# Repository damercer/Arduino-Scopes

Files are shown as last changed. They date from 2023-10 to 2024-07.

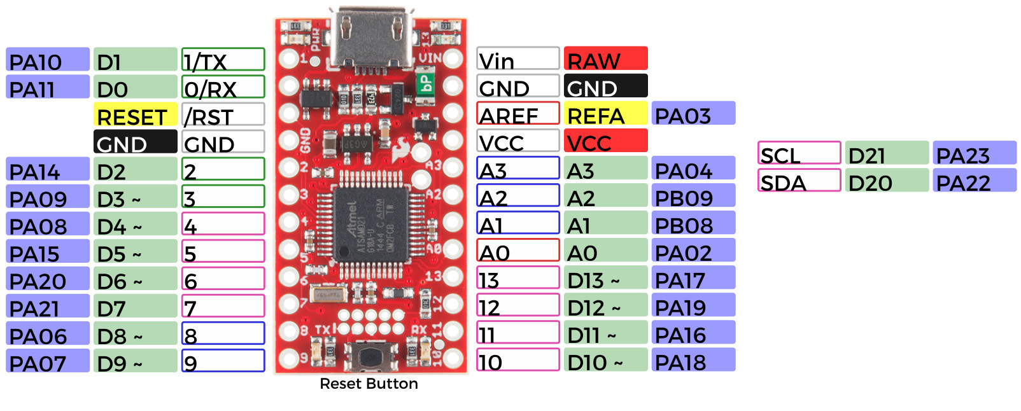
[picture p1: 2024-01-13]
SparkFun-SAMD21_pwm_awg/board-mini-overview-2.jpg

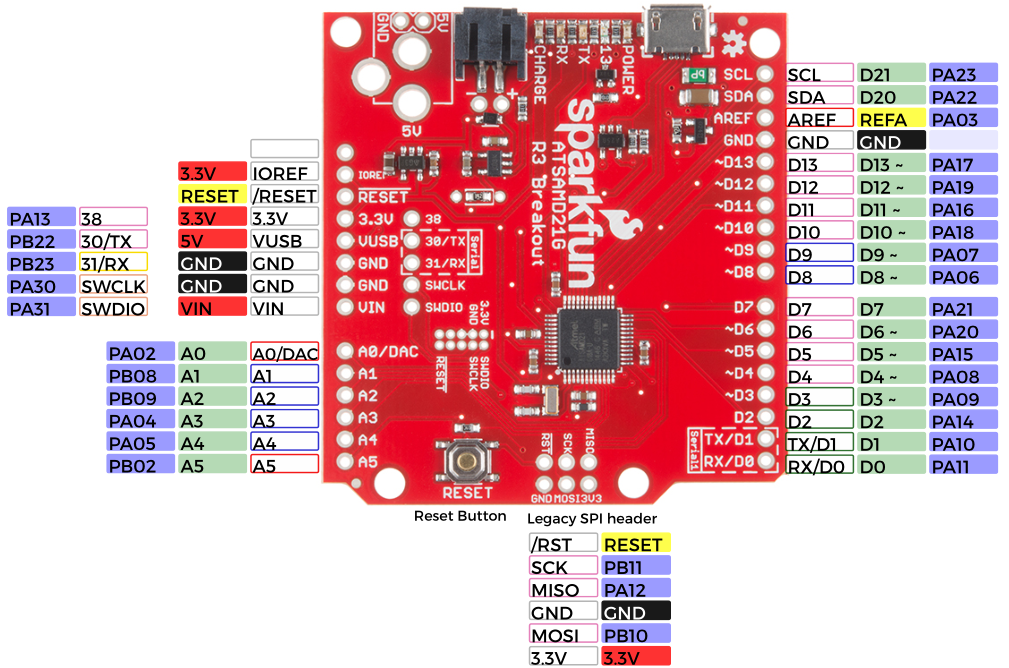
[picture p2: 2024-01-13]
SparkFun-SAMD21_pwm_awg/board-dev-overview.png

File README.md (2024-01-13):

# Arduino firmware for Universal-ALICE
With the goal of "Instrumentation for Every Student" in mind this project is intended to lower all barriers to providing a hardware and software platform for teaching electronic circuits to engineering students. Every student should have access to affordable hardware and software to measure their experiments.
This project offers a free open source software user interface that is compatible with hardware produced in large quantities at low cost (ranging from $5 to $20) from multiple suppliers.
#
Currently available hardware interfaces (some are works in progress):

* Arduino compatible microcontroler boards:
  + Adafruit QT Pi - SAMD21
  + Adafruit Trinket M0 (ATSAMD21)
  + Adafruit ItsyBitsy M0 Express (ATSAMD21)
  + Adafruit ItsyBitsy M4 Express (ATSAMD51)
  + Raspberry Pi Pico RP-2040
    - With external R/2R DAC or SPI DAC or PWM analog AWG output
  + SparkFun SAMD21 Mini Breakout (DEV-13664)
  + SparkFun Thing Plus - SAMD51 (DEV-14713)
  + Seeed Studio XIAO SAMD21
  + Seeed Studio XIAO RP-2040
    - With external SPI DAC or PWM analog AWG output

If you are not a technical individual or highly familiar with computer operating systems and you have your choice of computers, a Windows computer is highly recommended. You will usually run into fewer issues, if any, with that operating system.

Known Issues: If your computer encrypts files saved on external storge devices (USB disk drives) then the UF2 Bootloader method of flashing firmware to micro-controller boards will not work. You would need to use a different computer that does not encrypt files or consult your local system administrator.

Linux Operating system: On Linux computers access to USB based serial comms devices is not allowed for non root users by default. A udev rules file needs to be added. Place the 99-arduino.rules from this repository in etc/udev/rules.d

It contains one line per board / vendor:

SUBSYSTEMS=="usb", ATTRS{idVendor}=="802F", ATTRS{idProduct}=="2886", GROUP="dialout", MODE="0666"

The above idVendor value is board / vendor specific and may need to be adjusted to match your specific board(s). The one above is specifically for the XIAO SAMD21 board.

If this rules file does not work on your version of Linux there may be other things like this that work. Searching the web on how to make serial USB devices work may provide an alternate solution or consult with your local Linux expert.

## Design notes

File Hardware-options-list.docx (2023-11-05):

This Document.

This document lists various hardware options for very low cost personal instrumentation. These are listed in order by cost / ease of implementation / solderless breadboard friendliness.

Summary:

There are some basic assumptions.

First is that the hardware is part of the Arduino ecosystem and the embedded firmware is developed using the Arduino IDE.

Most all hardware platforms in the Arduino world have built in ADCs of some speed / resolution so any / all can provide a basic analog input / “oscilloscope” type instrument. They also generally provide at least one fixed DC power supply voltage available for the user. Digital inputs and outputs are available with one or more that can be programed as square wave PWM outputs.

Very few if any have internal DAC analog output(s) that could provide an analog waveform generator output (AWG) function. External components, such as serial (SPI) DAC integrated circuits, generally need to be added to generate analog waveforms. These add-on external circuits (modules) add cost and wiring complexity up to and including mounting everything on a carrier PCB which adds labor and cost.

As an alternate, but less desire able solution, analog outputs can be generated by modulating and low pass filtering one or more digital PWM outputs. The added cost could be as little as a passive resistor and capacitor but the output will not be buffered. A buffer op-amp or active filter circuit could be added.

The options presented here provide some solutions that provide various levels of cost, performance and complexity.

Version based on XIAO SAMD21

Performance Specs:

- Up to 3 12 bit Scope channels, 50 KSPS for one channel, 25 KSPS per channel for two channels or 16.667 KSPS for all three channels.
- One 8 bit AWG channel at 50 KSPS
- Up to 6 digital input channels at same sample rate as analog scope
- 1 PWM digital output or 1 PWM “analog” AWG output

Parts List: Total, $ 5.40 (plus import Tariff)

Seeed Studio XIAO SAMD21:

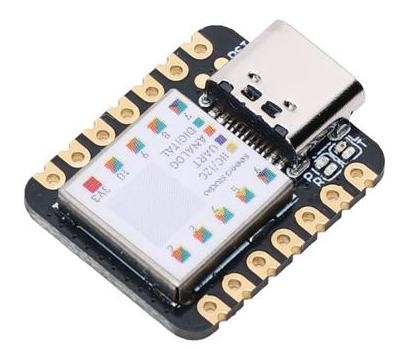
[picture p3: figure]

Many experiment setups can be done with just the one 14 pin module, so with installed male pin headers it can be easily inserted into a solderless breadboard and effectively becomes just another “part” in the experimental setup.

Solderless Breadboard Layout:

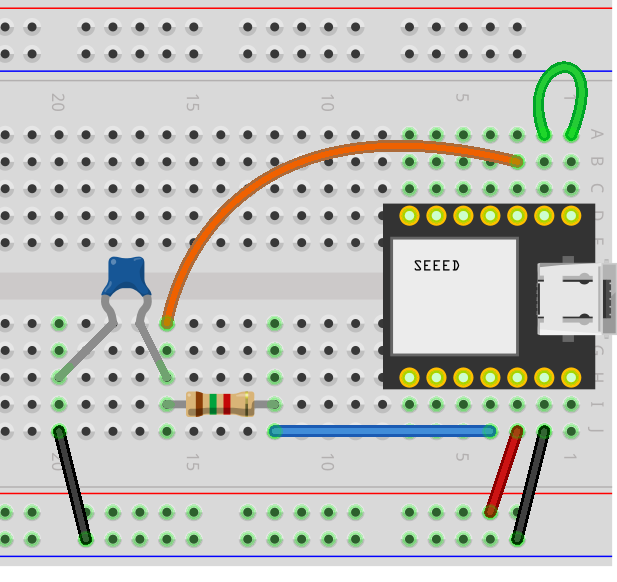
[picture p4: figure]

Includes RC low pass filter on PWM AWG output.

Version based on XIAO RP2040 + SPI DAC

Performance Specs:

- Up to 3 12 bit Scope channels at up to 200 KSPS for one channel, 125 KSPS for 2 channels, 83.333 KSPS for three channels.
- Up to two 8/10/12 bit AWG channels at 50 KSPS.
- Up to 4 digital input channels at same sample rate as analog scope.

Parts List: Total, $ 9.13 (plus import Tariff)

Seeed Studio XIAO RP2040:

- Price: Unit Price: $5.40 (plus import Tariff)
- Digi-Key Part Number: 1597-102010428-ND
- Manufacturer: Seeed Technology Co., Ltd
- Manufacturer Product Number: 102010428
- Description: SEEED STUDIO XIAO RP2040 ARDUINO

Dual DAC for AWG outputs: MCP4922-E/P

- Unit Price: $3.73
- Digi-Key Part Number, MCP4922-E/P-ND
- Manufacturer :Microchip Technology
- Manufacturer Product Number: MCP4922-E/P
- Description: IC DAC 12BIT V-OUT 14DIP

Alternate Dual DAC for AWG outputs: MCP4822-E/P

- Unit Price: $4.28
- Digi-Key Part Number, MCP4822-E/P-ND
- Manufacturer :Microchip Technology
- Manufacturer Product Number: MCP4822-E/P
- Description: IC DAC 12BIT V-OUT 8DIP

Alternate 10 and 8 bit dual DACs:

- MCP4812-E/P, $3.01
- MCP4802-E/P, $2.11
- LTC1661CN8, $5.43, 10BIT V-OUT 8DIP
- AD7303BNZ, $11.24, 8BIT V-OUT 8DIP

Again only the two components and some wires are used in this scheme so even more solderless breadboard friendly with the 14 pin XIAO module vs the 40 pin Pi Pico Module.

Solderless Breadboard Layout including two DAC reconstruction low pass filters.

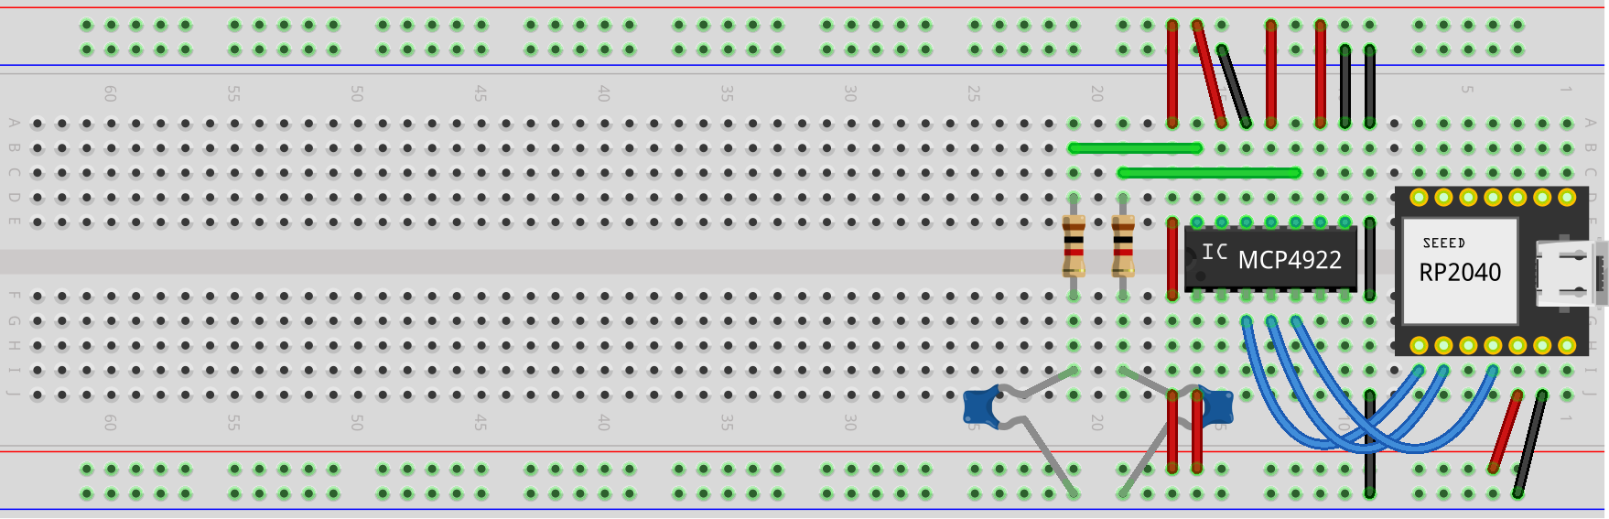
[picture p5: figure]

For relative size comparison.

The XIAO module along with SPI DAC could additionally be permanently mounted on a solder breadboard such as this one from Digi-Key: Cost $1.48.

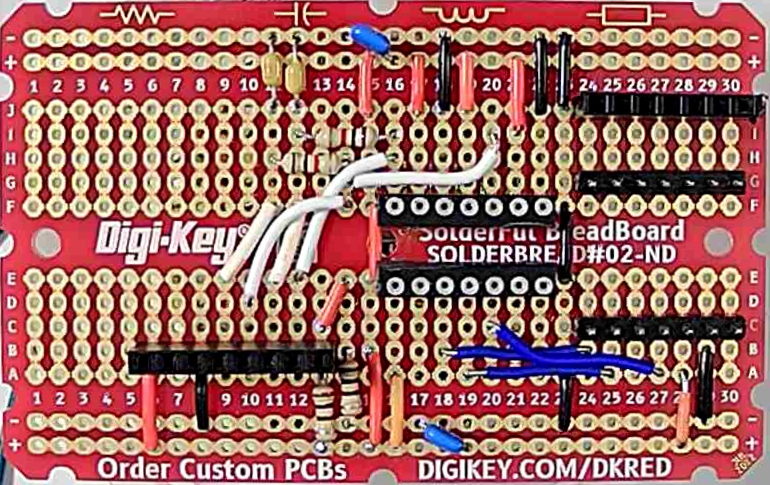
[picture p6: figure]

Solder breadboard wiring without active components installed

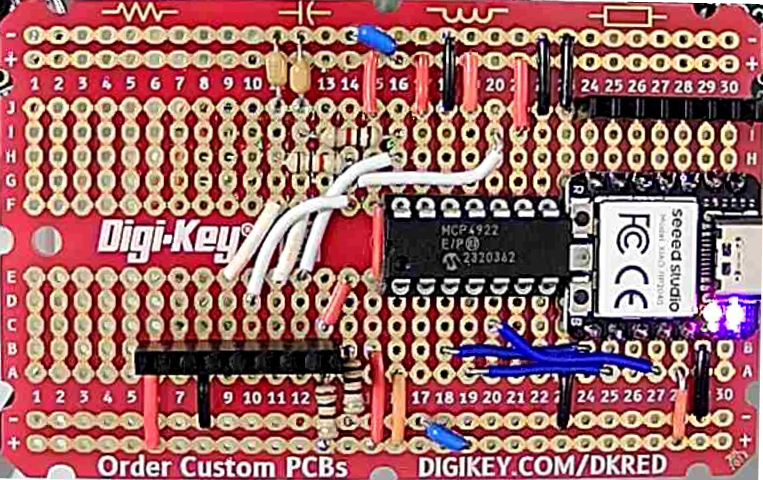
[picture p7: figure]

Solder breadboard wiring with active components installed

Digi-Key part number: DKS-SOLDERBREAD-02, 30 ROW SOLDERFUL BREADBOARD

Breadboard, General Purpose Plated Through Hole (PTH) 5 Hole Pad (Both Sides) 0.100" (2.54mm)

Version based on Raspberry Pi Pico + SPI DAC

Performance Specs:

- Up to 3 12 bit Scope channels at up to 200 KSPS for one channel, 125 KSPS for 2 channels, 83.333 KSPS for three channels.
- Up to two 8/10/12 bit AWG channels at 50 KSPS.
- Up to 8 digital input channels at same sample rate as analog scope.
- 1 PWM digital output.

Parts List: Total, $ 8.73 (plus import Tariff)

Raspberry Pi Pico RP2040 with headers:

- Unit price: $5.00 ($4.00 w/o headers)
- Digi-Key Part Number: 2648-SC0917-ND
- Manufacturer: Raspberry Pi, Manufacturer Product Number SC0917
- Description :RASPBERRY PI PICO H RP2040 Detailed Description :RP2040 Raspberry Pi Pico - ARM® Cortex®-M0+ MCU 32-Bit Embedded Evaluation Board

Dual DAC for AWG outputs: MCP4922-E/P

- Unit Price: $3.73
- Digi-Key Part Number, MCP4922-E/P-ND
- Manufacturer :Microchip Technology
- Manufacturer Product Number: MCP4922-E/P
- Description: IC DAC 12BIT V-OUT 14DIP

Alternate Dual DAC for AWG outputs: MCP4822-E/P

- Unit Price: $4.28
- Digi-Key Part Number, MCP4822-E/P-ND
- Manufacturer :Microchip Technology
- Manufacturer Product Number: MCP4822-E/P
- Description: IC DAC 12BIT V-OUT 8DIP

Alternate 10 and 8 bit dual DACs:

- MCP4912, MCP4812-E/P, $3.01
- MCP4902, MCP4802-E/P, $2.11
- LTC1661CN8, $5.43, 10BIT V-OUT 8DIP
- AD7303BNZ, $11.24, 8BIT V-OUT 8DIP

Only the two components and some wires are used in this scheme so somewhat solderless breadboard friendly.

Solderless breadboard layout (minus DAC reconstruction filter):

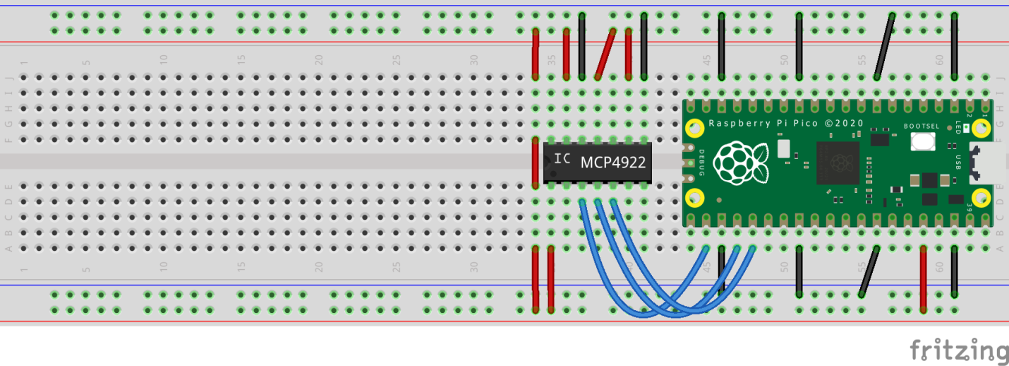
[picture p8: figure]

For relative size comparison. About ½ of a full length breadboard is needed.

Version based on Raspberry Pi Pico + Resistor Networks

Performance Specs:

- Up to 3 12 bit Scope channels at up to 200 KSPS for one channel, 125 KSPS for 2 channels, 83.333 KSPS for three channels.
- Up to two 8 bit AWG channels at 100 KSPS
- Up 6 digital input channels at same sample rate as analog scope
- 1 PWM digital output

List of Hardware:

Total parts cost less than $10 not including any PCB to mount parts on or a full length solderless breadboard.

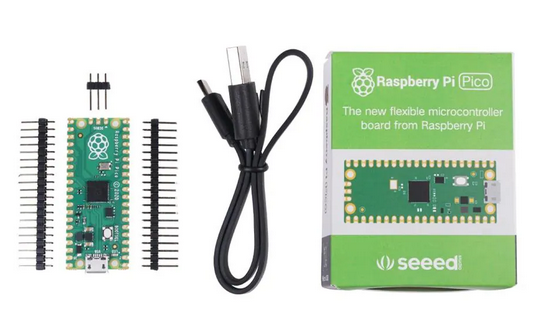
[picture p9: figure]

Pi Pico Board Basic Kit $6.38 each or $4.00 for just board no headers or $5.00 with installed headers: (SC0915 Description RASPBERRY PI PICO RP2040)

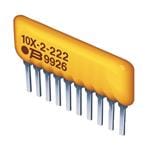
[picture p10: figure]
Bourns 4606X-R2R-103LF Enlarged Image

2X - 10 K R/2R ladder network for AWG DACs $ 0.51 each (4606X-R2R-103LF) at Mouser $0.71 at Digi-Key

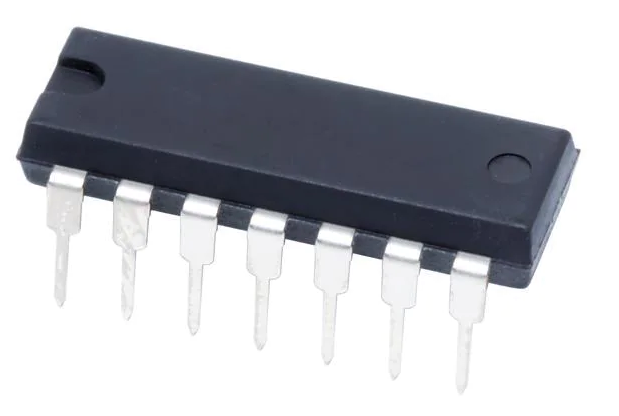
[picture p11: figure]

2X - LM324 Quad Op-amp for AWG DAC buffers / Scope Input buffers $0.59 each at Mouser $0.11 at Digi-Key

Up to 16 – 20 1/8 watt resistors various values.

Not particularly solderless breadboard friendly so a PCB to mount everything will be a useful approach.

PC Board Layout:

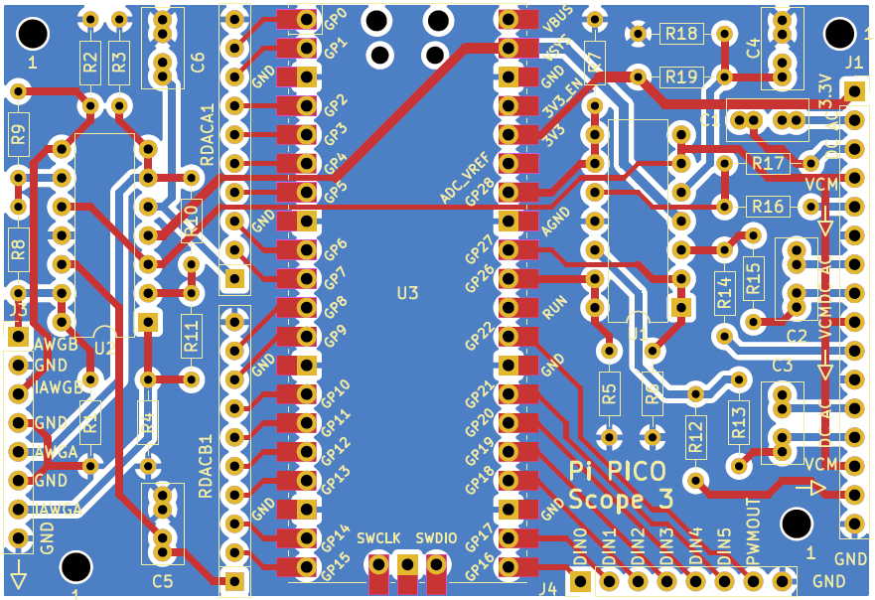
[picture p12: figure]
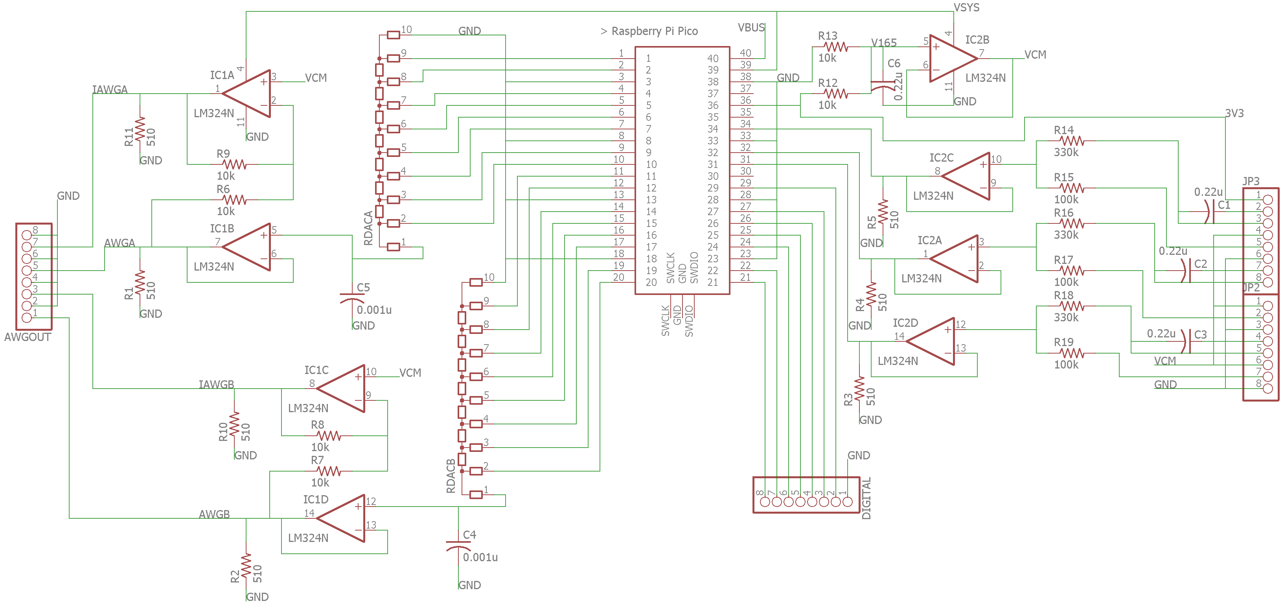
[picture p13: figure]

PCB Schematic

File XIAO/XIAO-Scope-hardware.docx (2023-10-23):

Seeed Studio XIAO SAMD21 as an introductory personal instrument.

Objective:

To demonstrate the use of the Seeed Studio XIAO SAMD21 micro-controller board as a personal lab data measurement system in introductory level circuits (and electronics) courses.

Hardware:

Seeed Studio XIAO SAMD21 micro-controller board. Cost $5.40 (Digi-Key Part Number 1597-102010328-ND)

The XIAO board is a small 14 pin DIP like module. By installing male pin headers it can be easily inserted into a solderless breadboard and effectively becomes just another “part” in the experimental setup.

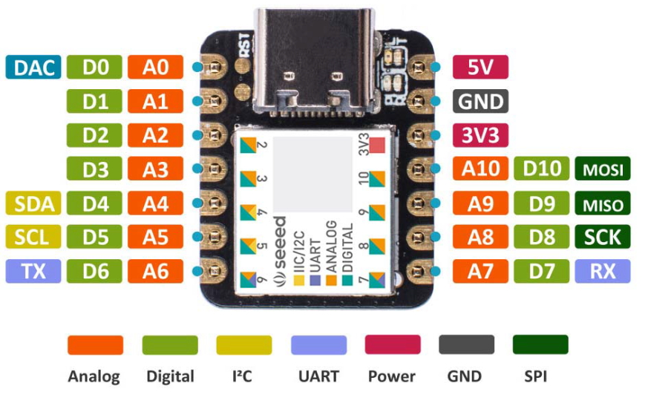
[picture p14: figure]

XIAO pinout

The XIAO contains one 12 bit ADC which can be multiplexed to multiple pins. It also contains one 10 bit DAC available on pin A0. The overall maximum ADC sample rate (50 KSPS) will be shared by the scope input channels and the per channel sample rate will depend on the number of analog input pins being measured. The XIAO can also generate a PWM digital output on pin D10. This PWM output can also be modulated and low pass filtered to provide a pseudo second AWG output channel (B). Using the PWM output as a second AWG output will cut the analog DAC sample rate essentially in half.

The remaining 6 digital input pins (D4 – D9) can optionally be sampled along with the analog inputs to provide a kind of “mixed signal” scope display.

None of the XIAO pins are 5 V tolerant and will likely be damaged if voltages beyond 0 and 3.3V are applied. The XIAO SAMD21 is a 3.3 volts device and applying 5 volts to an input will overload and damage the XIAO. There may be a 5-volt power connection on the board, but DO NOT use it to power experiments unless you are certain of the voltages of any nodes you might be measuring with one of the input pins. Absolute Maximum Pin voltage with respect to GND - GND-0.6V and VDD - VDD+0.6V.

USB C to USB A cable.

Solderless breadboard.

Various components, resistors, capacitors, diodes …

Board Firmware:

Developed using the Arduino IDE.

Download the Arduino IDE from here: https://www.arduino.cc/en/software

Seeed Studio Getting Started web page (contains info on configuring Arduino IDE for XIAO): https://wiki.seeedstudio.com/Seeeduino-XIAO/

How to Add Seeed boards to Arduino IDE: (from https://wiki.seeedstudio.com/Seeed_Arduino_Boards/)

Open the Arduino IDE, click on File > Preferences, and copy the below url to the Additional Boards Manager URLs list:

https://files.seeedstudio.com/arduino/package_seeeduino_boards_index.json

Click on Tools > Board > Board Manager. Now search the board by name, “Seeeduino XIAO”

Click on Tools > Ports and select the correct COM port for the board.

Open the Source file: XIAO_Scope_pwm_awg.ino

Click on the Upload arrow button.

PC Host Software:

ALICE Universal, PC Host User Interface developed using Python 3.10 and XIAO hardware specific interface code also developed using Python 3.10 (PySerial library required). Source code and configuration files:

Alice-universal-alpha.pyw

alice_init.ini

XIAO_3a_1w_6d_Interface_Level.py

Demonstration Lab Examples:

The test circuit schematic shown in figure 1 and breadboard layout shown in figure 2 is used to illustrate how the micro-controller hardware is connected to a simple R-C low pass circuit. The R-C test circuit consists of R1 and C1. The “grounded” end of C1 is connected to a resistor divider (R2 and R3) between GND (black wire) and the 3.3V power supply (red wire).

The voltage at the divider will be 3.3V / 2 or about 1.65 V. The equivalent resistance seen at the divider node will be 100Ω / 2 or about 50Ω.

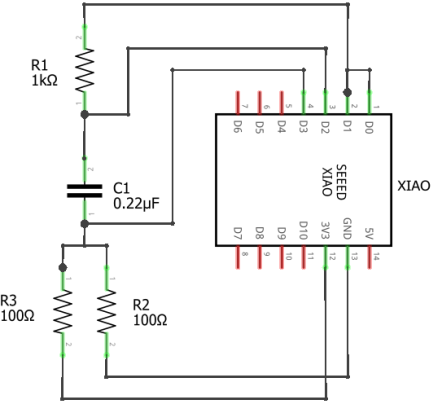
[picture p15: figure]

Figure 1, Simple R-C test circuit.

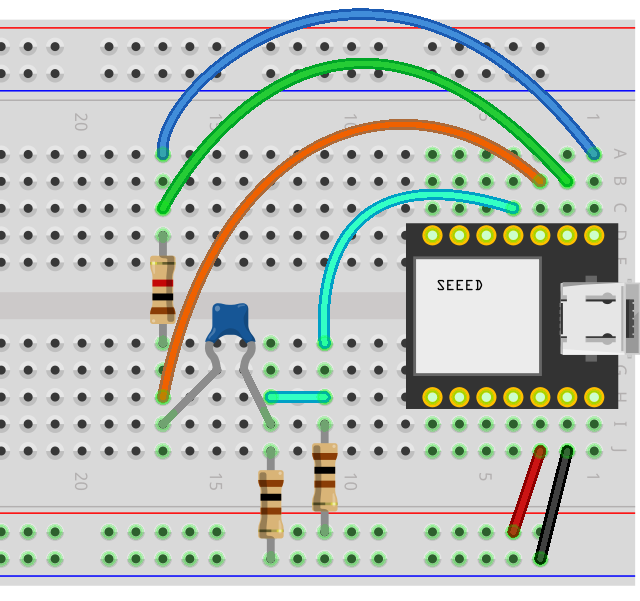
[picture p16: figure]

Figure 2, R-C Solderless Breadboard layout.

The A0 pin on the XIAO is the DAC output which provides the AWG (A) function generator output. The A1, A2 and A3 pins on the XIAO are used for the three Scope input channels (CH A, CH B and CH C respectively).

Figure 3 shows the waveform traces as displayed in ALICE. The AWG output is set to generate a 2.8 V p-p sine wave at 300 Hz. The green trace is the green wire in figure 2, the orange trace is the orange wire and the cyan trace is the cyan wire. The p-p voltage seen at the resistor divider junction divided by the 50Ω equivalent resistance is the current in capacitor C1 (about 1.1mA p-p in this example).

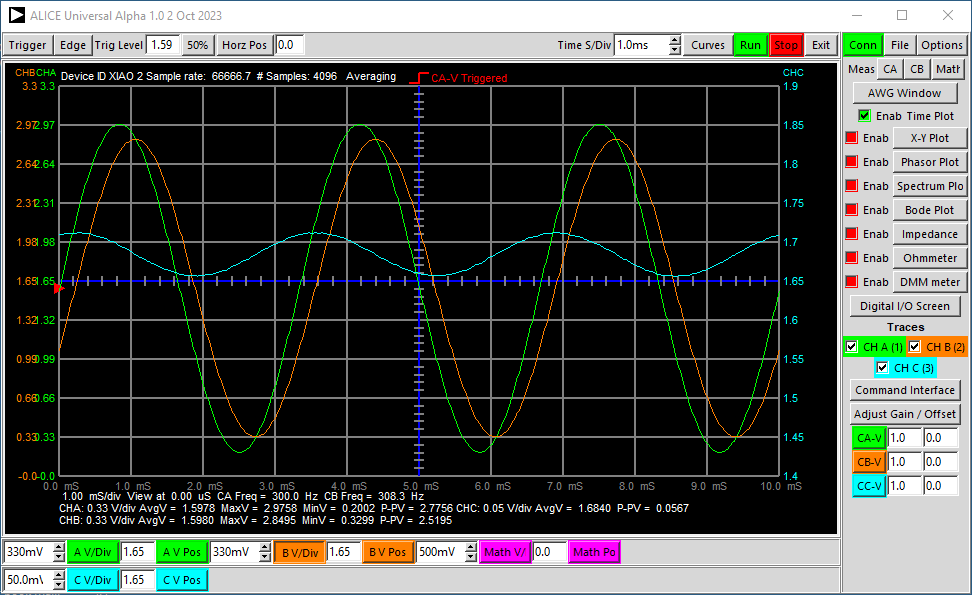
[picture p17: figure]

Figure 3, R-C test User interface screen shot.

Using essentially the same breadboard circuit as in Figure 2 we can plot the I/V curve of a diode. We replace C1 with diode D1 (1N914 or similar) and change the value of R1 to 150Ω, as in figures 4 and 5. The DAC output is set to generate a 122 Hz triangle waveform that swings the maximum voltage from nearly 0 to 3.2 V. Again we reference the “negative” end of the diode to the ½ supply divider to apply positive and negative voltages across the diode.

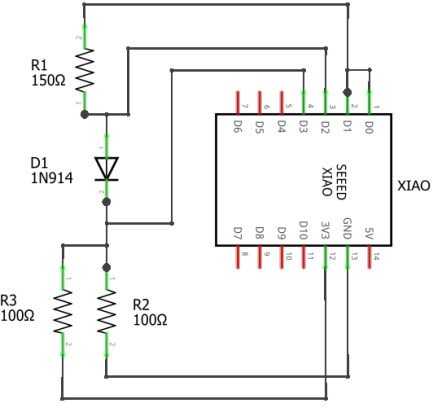
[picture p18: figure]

Figure 4, Diode I/V test circuit.

We can use the X,Y plotting tool in ALICE to calculate the current in the diode and plot it vs the voltage across the diode as shown in the figure 6 X,Y window screen shot. The vertical Y axis is scaled in mA. The horizontal axis has been shifted to be centered on 0 V across the diode.

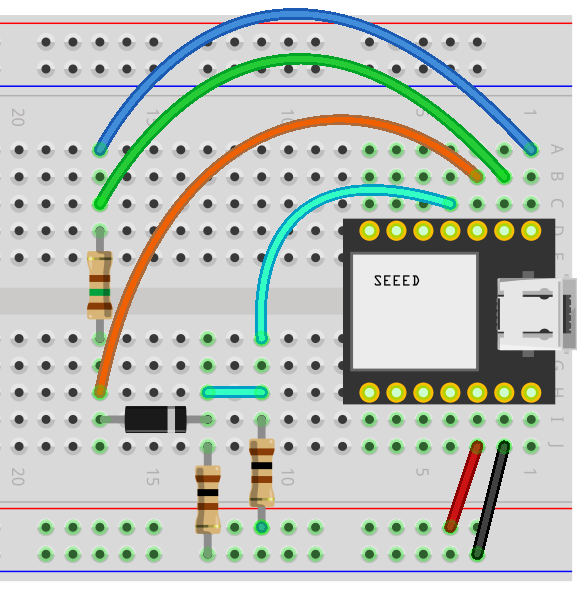
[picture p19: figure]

Figure 5, Diode I/V breadboard layout.

We use the Math controls in ALICE to calculate the diode current with the following formula for the Math-X trace:

(VBuffA-VBuffB)*6.6667

Where VBuffA is the voltage on the top of R1 and VBuffB is the voltage on the bottom of R1. We get the voltage across R1 by subtracting the two voltages. The current in mA is scaled by multiplying the difference voltage by 1000/150Ω or 6.6667.

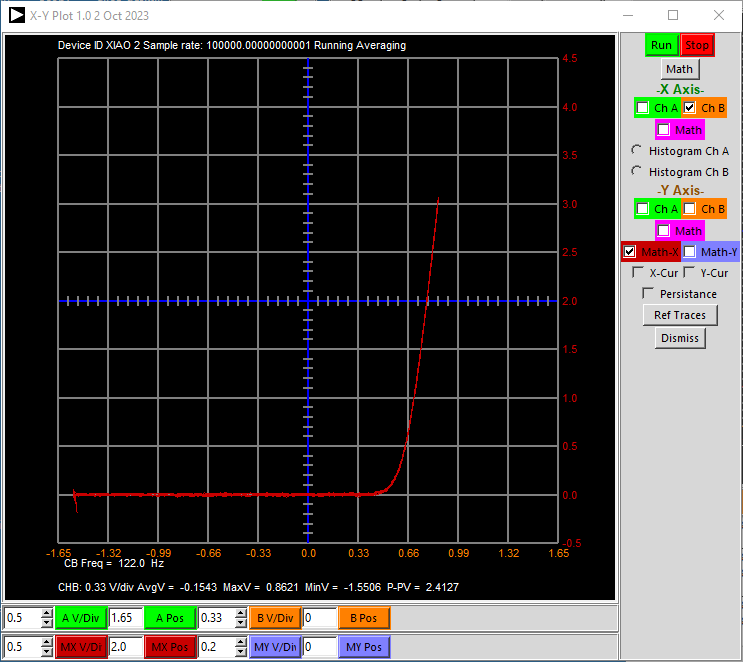
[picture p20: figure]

Figure 6, Diode I/V plot.

As a third example test circuit we have an inverting and non-inverting gain of 1 NPN amplifier (the so called “phase splitter”) shown in figure 7. The circuit consists of one NPN transistor (2N3904 or similar) and two 1kΩ resistors. R1 is the collector load resistor and R2 is the emitter resistor. The amplifier input signal from the AWG generator is connected to the base of the transistor. The gain from base to emitter (non-inverting) is +1 as the transistor is acting as an emitter follower. Since R1 and R2 are equal the (inverting) gain from base to collector is -1.

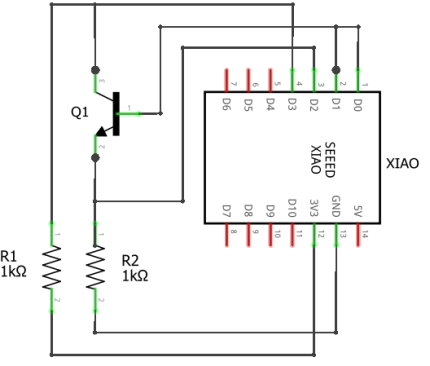
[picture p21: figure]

Figure 7, NPN Amplifier schematic

In the breadboard layout shown in figure 8, the AWG output is connected to the base of the transistor (blue wire) and the waveform Shape is a sine wave at 400 Hz. The Min and Max voltage values are adjusted such that neither of the output signals, at the collector or at the emitter, are clipped. We can use the three scope input channels to monitor the input signal at the base (CH A green wire) and the two output signals at the emitter (orange wire) and at the collector (cyan wire) as shown.

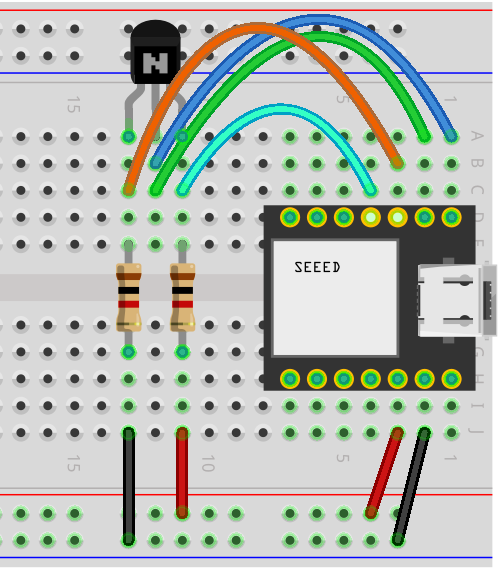
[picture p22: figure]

Figure 8, NPN Amplifier breadboard layout.

In figure 9 we see the three scope traces. There is a DC level shift from the input to the respective outputs but the p-p amplitude is nearly the same at gains of +1 to the emitter (orange trace) and -1 to the collector (cyan trace).

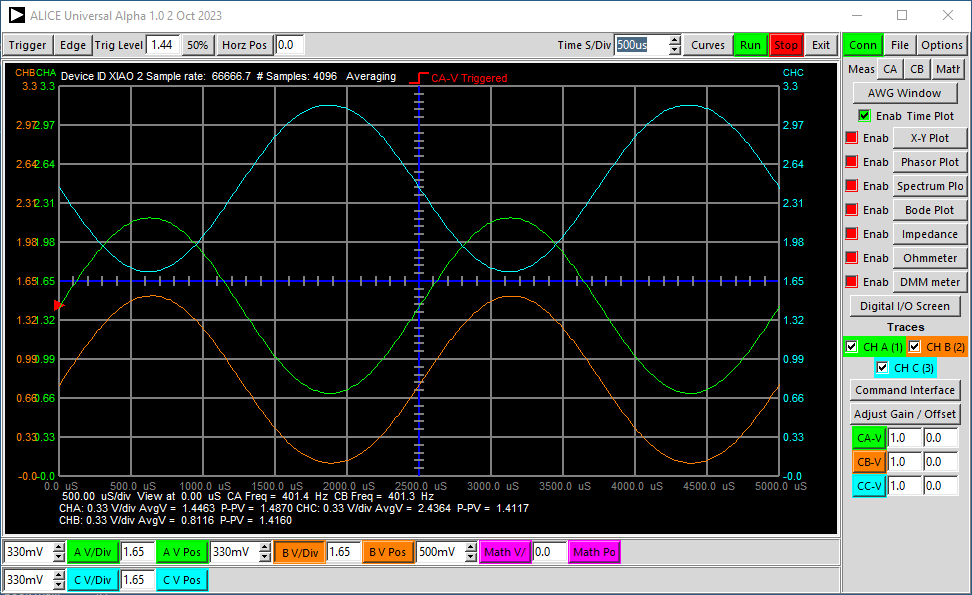
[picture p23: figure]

Figure 9, NPN Amplifier Scope traces.

PWM Output as Second AWG Channel:

The PWM digital output on pin D10 can be modulated with analog waveform samples to generate a second AWG output channel. The PWM switching frequency is set at 64 KHz which is well above the scope sampling frequency and beyond the input bandwidth and cannot be directly viewed using the scope input.

The PWM signal of course needs to be low pass filtered to reconstruct the analog waveform. A simple R-C filter as shown in figure 10 is sufficient for low frequency waveforms. In the example schematic the analog DAC output AWG (on pin A0) is measured using Scope CH A (on pin A1) for reference purposes. The D10 output is filtered by R1, 1.5kΩ, and C1, 0.22µF. The filtered output is measured by Scope CH B (on pin A2).

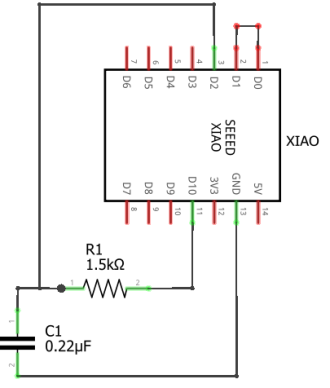
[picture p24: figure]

Figure 10, R-C low pass filtered PWM output AWG channel.


Figure 11, PWM output AWG channel breadboard layout.

For comparison purposes the analog DAC output AWG is displayed on Scope CH A (green trace) and the filtered PWM AWG output is displayed on CH B (orange trace), figure 12. Both are generating a 150 Hz sine wave. The Min and Max values of the PWM channel were adjusted to approximately match the AWG A output amplitude and offset. The digital output is not going to produce an exact 0 to 3.3 V swing. The R-C filter time constant introduces a phase delay in channel B but that could be corrected for by introducing an appropriate phase shift in the AWG waveform data samples.

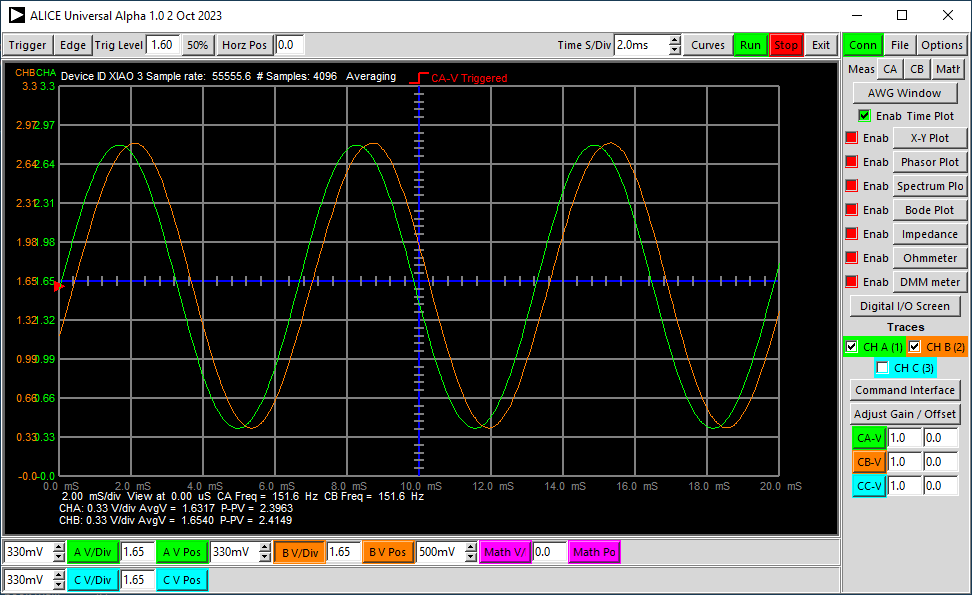
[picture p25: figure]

Figure 12, R-C low pass filtered PWM output AWG waveform.

Note that modulating the PWM output takes considerable extra CPU cycles and thus the ADC (Scope) sample rate, even for just two scope channels, is significantly reduced.

Input Dividers for voltages greater than 0 to 3.3V:

The relatively high input impedance (measured as ~2MegΩ) of the XIAO allows the use of relatively simple resistive input dividers. Example dividers are shown in figure 13. The 220kΩ and 2 100kΩ parallel resistors combine to make an input scale factor of ~5.5:1 with an offset that centers the allowed peak to peak input swing of 5.5 X 3.3 V ~ 18 V on 1.65 V (-16.35 to 19.65). The input resistance will be 220kΩ + 50kΩ or 270kΩ. The relatively high 220kΩ value of the input resistor inherently limits the current that might flow into the XIAO input pin during over voltage conditions.

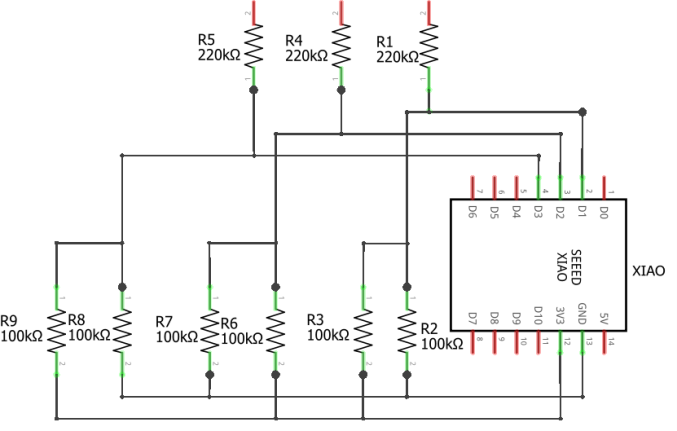
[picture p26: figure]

Figure 13, Input resistor voltage divider example

Other resistor values and combinations are of course possible but it is best to keep the effective resistance seen at the XIAO input pins no greater than 50k to 100k.

ALICE provides an input resistor divider calculator tool as shown in figure 14. The resistor value to enter for R1 in the above example is of course the 220k. The resistor value to enter for R2 is the parallel combination of the two 100kΩ resistors or 50kΩ. The offset voltage value to enter will be 3.3 V / 2 or 1.65 because the 100kΩ resistors are connected to both GND and 3.3V.


Figure 14, ALICE resistor input divider gain calculator


Figure 15, Dividers included on a solderless breadboard

The XIAO module along with any input resistor dividers could additionally be permanently mounted on a solder breadboard such as this one from Digi-Key: Cost $1.48.


Digi-Key part number: DKS-SOLDERBREAD-02, 30 ROW SOLDERFUL BREADBOARD

Breadboard, General Purpose Plated Through Hole (PTH) 5 Hole Pad (Both Sides) 0.100" (2.54mm)

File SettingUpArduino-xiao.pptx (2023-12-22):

## Steps to programming the Seeed Studio XIAO SAMD21

## The Arduino IDE

The first step is to download and install the Arduino IDE for your operating system which can done from here:
https://www.arduino.cc/en/software
Generally, you can skip the various donation and email subscription options and press the “Just Download” buttons.


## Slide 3

Create a folder on your computer named: XIAO_Scope_pwm_awg
Download this file to that new folder:
https://github.com/damercer/Arduino-Scopes/blob/main/XIAO/XIAO_Scope_pwm_awg/XIAO_Scope_pwm_awg.ino
In the (newly installed) Arduino IDE, pull down file to Open and open this INO file.


## In the IDE, pull down File to Preferences and click on the “Additional URLs” button.


## Copy and paste the following URL into the edit window and click OK. https://files.seeedstudio.com/arduino/package_seeeduino_boards_index.json


1

2

Click OK to accept this preference change.

3

## Open the Boards Manager and type “Seeed SAMD” in the Search bar and click INSTALL.


2

1

3

Search

Boards Manager

Install

## Plug the board into a USB port.


The green Power LED should be on.
Note: A new board fresh from the factory will probably be running the “Blink” program where the orange LED slowly blinks.

## Select the board from the board manager.


Check Mark Here

## Select the COM port for the Arduino. (Your port number may vary.)


Check Mark Here

## Confirm port selection in the lower right-hand corner of the IDE.


## Click on the right pointing arrow to compile and upload the software to the board.


## Confirmation of the upload.


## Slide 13

Confirm Board is functioning.

1- In the Arduino IDE, in the upper right corner, click on the icon that looks like a circle with a dot to open the serial monitor.


1

2- Type a capital I (eye) + Enter in the text entry line which appears in the middle of the screen.


2

3- The board will respond, confirming that the code is loaded and running,

3

Just the Green Power LED should be on.
Note: The Blue LED will flash whenever the PC communicates with the board.

## The XIAO SAMD21 board is now programmed to work with Universal ALICE GUI.

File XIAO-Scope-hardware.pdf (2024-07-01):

Seeed Studio XIAO SAMD21 as an introductory personal instrument.

Objective:

To demonstrate the use of the Seeed Studio XIAO SAMD21 micro-controller board as a personal lab data measurement system in introductory level circuits (and electronics) courses. The main intended audience of this document is instructors wishing to learn the capabilities of the hardware and software. Parts of the document could be adapted for use by students as a starting introduction to the hardware and software.

Hardware:

Seeed Studio XIAO SAMD21 micro-controller board. Cost $5.40 (Digi-Key Part Number 1597-102010328-ND)

The XIAO board is a small 14 pin DIP like module. By installing male pin headers it can be easily inserted into a solderless breadboard and effectively becomes just another “part” in the experimental setup.

Power Supplies and Ground; PWM Output Scope CH D

XIAO pinout

The XIAO contains one 12 bit ADC which can be multiplexed to multiple pins. It also contains one 10 bit DAC available on pin A0. The overall maximum ADC sample rate (~100 KSPS) will be shared by the scope input channels and the per channel sample rate will depend on the number of analog input pins being measured. The sample rate of the internal 10 Bit DAC is roughly 70 KSPS or 14 microseconds. The XIAO can also generate a PWM digital output on pin D10. This PWM output (at 93.750 kHz) can also be modulated with 9 bit resolution samples at the same rate as the DAC. The PWM output is then low pass filtered to provide a pseudo second AWG output channel (B).

None of the XIAO pins are 5 V tolerant and will likely be damaged if voltages beyond 0 and 3.3V are applied. The XIAO SAMD21 is a 3.3 volts device and applying 5 volts to an input will overload and damage the XIAO. There may be a connection on the board to the 5 volt USB power, but DO NOT use it to power experiments unless you are certain of the voltages of any nodes you might be measuring with one of the input pins. Absolute Maximum Pin voltage with respect to GND - GND-0.6V and VDD -VDD+0.6V.

Extra required materials, USB A to USB C cable, Solderless breadboard, various components, resistors, capacitors, diodes, transistors …

AWG Output

Scope CH A
Scope CH B
Scope CH C

Board Firmware:

Developed using the Arduino IDE.

The firmware file XIAO_Scope_pwm_awg.uf2 from Zip archive.

To load the .uf2 firmware file, the board needs to be put into the UF2 Bootloader. There are a couple of ways to accomplish this. Some are more difficult than others. Choose the one that seems the easiest to do for you.

Method 1: With the board plugged into a USB port and powered up, use a wire jumper to short the two small round pads, labeled RST, to the left of the USB C connector as shown below. Short the pads twice quickly, i.e. tap, to put the board into the bootloader. The amber (yellow) LED will flash and then go into a slow “breathing” mode.


Placing board into bootloader Method 1

An external USB drive folder should pop up like this:

External drive folder Arduino (E:)

Method 2: Using a serial terminal program, such as PuTTY on Windows, connect to the board’s serial port at 1200 Baud and then close the connection by exiting the serial terminal program. (On Windows the COM port number can be found using the Device Manager). The external USB drive folder should pop up as in Method 1.


Placing board into bootloader Method 2

Copy and paste the firmware file XIAO_Scope_pwm_awg.uf2 on to this new USB drive (Drag and Drop works). The drive window will close (disappear) and the yellow LED will go out and just the green power LED will be on. The board is now programed with the firmware and ready to use.

Method 3: Use ALICE PC Host software, See Below.

Alternatively the Arduino source code can be compiled and up loaded to the board using the Arduino IDE. Source code sketch from here:

https://github.com/damercer/Arduino-Scopes/tree/main/XIAO_Scope_pwm_awg

PC Host Software:

ALICE Universal, PC Host User Interface (numpy library required) developed using Python 3.10 and XIAO SAMD21 hardware specific interface code also developed using Python 3.10 (installing the pyserial library is required). Source code and configuration files (ALICE Users Guide is in same repository) contained in this .zip file:

Alice-universal-alpha.pyw
XIAO_4a_1w_pwm_Interface_Level.py
alice_init.ini
alice-last-config.cfg

At the moment for Windows based computers the ALICE program can up load the firmware file XIAO_Scope_pwm_awg.uf2 to XIAO SAMD21 boards that are not already programed. The .uf2 file must be in the same folder with the Python program(s). External disk drive letter E: must be available, that is, it is not being used by another storage device like a CD/DVD drive or USB drive.

On other Operating systems, at the moment, the program will only place the board in the Bootloader. An external USB drive folder should pop up and the User must manually copy the .uf2 file to the external USB drive as above.

Set Serial port Baud Rate to 1200 here

Set Serial COM port number here from Device manager

Click Open then Exit the program

Demonstration Lab Examples:

The test circuit schematic shown in figure 1 and breadboard layout shown in figure 2 is used to illustrate how the micro-controller hardware is connected to a simple R-C low pass circuit. The R-C test circuit consists of R1 and C1. The “grounded” end of C1 is connected to a resistor divider (R2 and R3) between GND (black wire) and the 3.3V power supply (red wire).

The voltage at the divider will be 3.3V / 2 or about 1.65 V. The equivalent resistance seen at the divider node will be 100Ω / 2 or about 50Ω.


Figure 1, Simple R-C test circuit.


Figure 2, R-C Solderless Breadboard layout.

The A0 pin on the XIAO is the DAC output which provides the AWG (A) function generator output. The A1, A2 and A3 pins on the XIAO are used for the three Scope input channels (CH A, CH B and CH C respectively).

Figure 3 shows the waveform traces as displayed in ALICE. The AWG output is set to generate a 2.8 V p-p sine wave at 300 Hz. The green trace is the green wire in figure 2, the orange trace is the orange wire and the cyan trace is the cyan wire. The p-p voltage seen at the resistor divider junction divided by the 50Ω equivalent resistance is the current in capacitor C1 (about 1.1mA p-p in this example).


Figure 3, R-C test User interface screen shot.

Using essentially the same breadboard circuit as in Figure 2 we can plot the I/V curve of a diode. We replace C1 with diode D1 (1N914 or similar) and change the value of R1 to 150Ω, as in figures 4 and 5. The DAC output is set to generate a 122 Hz triangle waveform that swings the maximum voltage from nearly 0 to 3.2 V. Again we reference the “negative” end of the diode to the ½ supply divider to apply positive and negative voltages across the diode.


Figure 4, Diode I/V test circuit.

We can use the X-Y plotting tool in ALICE to calculate the current in the diode and plot it vs the voltage across the diode as shown in the figure 6 X-Y window screen shot. The vertical Y axis is scaled in mA. The horizontal axis has been shifted to be centered on 0 V across the diode.


Figure 5, Diode I/V breadboard layout.

We use the Math controls in ALICE to calculate the diode current with the following formula for the Math-X trace:

(VBuffA-VBuffB)*6.6667

Where VBuffA is the voltage on the top of R1 and VBuffB is the voltage on the bottom of R1. We get the voltage across R1 by subtracting the two voltages. The current in mA is scaled by multiplying the difference voltage by 1000/150Ω or 6.6667.

Figure 6, Diode I/V plot.

As a third example test circuit we have an inverting and non-inverting gain of 1 NPN amplifier (the so called “phase splitter”) shown in figure 7. The circuit consists of one NPN transistor (2N3904 or similar) and two 1kΩ resistors. R1 is the collector load resistor and R2 is the emitter resistor. The amplifier input signal from the AWG generator is connected to the base of the transistor. The gain from base to emitter (non-inverting) is +1 as the transistor is acting as an emitter follower. Since R1 and R2 are equal the (inverting) gain from base to collector is -1.


Figure 7, NPN Amplifier schematic

In the breadboard layout shown in figure 8, the AWG output is connected to the base of the transistor (blue wire) and the waveform Shape is a sine wave at 400 Hz. The Min and Max voltage values are adjusted such that neither of the output signals, at the collector or at the emitter, are clipped. We can use the three scope input channels to monitor the input signal at the base (CH A green wire) and the two output signals at the emitter (orange wire) and at the collector (cyan wire) as shown.


Figure 8, NPN Amplifier breadboard layout.

In figure 9 we see the three scope traces. There is a DC level shift from the input to the respective outputs but the p-p amplitude is nearly the same at gains of +1 to the emitter (orange trace) and -1 to the collector (cyan trace).


Figure 9, NPN Amplifier Scope traces.

PWM Output as Second AWG Channel:

The PWM digital output on pin D10 can be modulated with analog waveform samples to generate a second AWG output channel. The PWM switching frequency is set at 93.750 kHz which is above the scope sampling frequency (50 KSPS each for two channels in this example) and beyond the input bandwidth and cannot be directly viewed using the scope input.

The PWM signal of course needs to be low pass filtered to reconstruct the analog waveform. A simple R-C filter as shown in figure 10 is sufficient for low frequency waveforms. In the example schematic the analog DAC output AWG (on pin A0) is measured using Scope CH A (on pin A1) for reference purposes. The D10 output is filtered by R1, 1.5kΩ, and C1, 0.22µF. The filtered output is measured by Scope CH B (on pin A2).


Figure 10, R-C low pass filtered PWM output AWG channel.

Figure 11, PWM output AWG channel breadboard layout.

For comparison purposes the analog DAC output AWG is displayed on Scope CH A (green trace) and the filtered PWM AWG output is displayed on CH B (orange trace), figure 12. Both are generating a 150 Hz sine wave. The Min and Max values of the DAC channel is set to 0.2 and 3.0 V and the PWM channel was adjusted to approximately match the AWG A output amplitude and offset at 0.12 and 3.11 V. The digital output is not going to produce an exact 0 to 3.3 V swing. The R-C filter time constant introduces a phase delay in channel B but that could be corrected for by introducing an appropriate phase shift in the PWM waveform data samples with respect to the DAC waveform.


Figure 12, R-C low pass filtered PWM output waveform vs DAC waveform.

## Note:

Care should be taken to insure that the Scope inputs are never connected to voltages greater than 3.3 V such as the nearly 5 V supply rail that is also available on the XIAO module. The Scope inputs can be made “5V Tolerant” by inserting a resistor of at least 5kΩ (4.7kΩ or 5.1kΩ) between the XIAO module pin and the circuit node being measured. The added series resistance will have a negligible effect owing to the relatively high impedance of the ADC inputs but limit the current to a safe level.

Input Dividers for voltages beyond 0 to 3.3V:

The relatively high input impedance of the XIAO module allows the use of relatively simple resistive input dividers. Example dividers are shown in figure 13. The 220kΩ and 2 100kΩ parallel resistors combine to make an input scale factor of ~5.5:1 with an offset that centers the allowed peak to peak input swing of 5.5 X 3.3 V ~ 18 V on 1.65 V (-16.35 to 19.65). The input resistance will be 220kΩ + 50kΩ or 270kΩ. The relatively high 220kΩ value of the input resistor inherently limits the current that might flow into the XIAO input pin during over voltage conditions.


Figure 13, Input resistor voltage divider example

Other resistor values and combinations are of course possible but it is best to keep the effective resistance seen at the XIAO input pins no greater than 50k and actually the lower the better. If a higher resistance divider is requited then an op-amp buffer should be placed between the divider output and the XIAO ADC (Scope) inputs.

ALICE provides an input resistor divider calculator tool as shown in figure 14. The resistor value to enter for R1 in the above example is of course the 220k. The resistor value to enter for R2 is the parallel combination of the two 100kΩ resistors or 50kΩ. The offset voltage value to enter will be 3.3 V / 2 or 1.65 because the 100kΩ resistors are connected to both GND and 3.3V.


Figure 14, ALICE resistor input divider gain calculator


Figure 15, Dividers included on a solderless breadboard

The XIAO module along with any input resistor dividers could additionally be permanently mounted on a solder breadboard such as this one from Digi-Key: Cost $1.48.


Digi-Key part number: DKS-SOLDERBREAD-02, 30 ROW SOLDERFUL BREADBOARD

Breadboard, General Purpose Plated Through Hole (PTH) 5 Hole Pad (Both Sides) 0.100" (2.54mm)

Effects of Source Impedance Test:

Unlike more complete (more costly) solutions these MCU breakout boards do not include any of the analog signal processing chain often built into more advanced data acquisition hardware. The raw input of the internal ADC is not buffered and the charge redistribution nature of the ADC presents finite impedance to the circuit being measured. This input impedance will be in parallel with any impedance of the node being measured and will affect the results (such as using external resistor dividers as discussed above).

To demonstrate this effect the following experiment can be done. By inserting various resistors in series with the AWG output we can change the source impedance and see the effect. Connect the AWG output to 1kΩ, 10kΩ and 100kΩ resistors as shown in figure 16. Scope channel A is connected directly to the AWG output with no series resistance to be used for comparison. Scope channel B is connected to the AWG output through one of the three series resistors.

Figure 16, Source Impedance Test.

The following series of Scope plots show the Channel A and B traces (green and orange) and the Math trace of CHA – CHB to show the difference between the two for the three different series resistors, 1kΩ, 10kΩ and 100kΩ.


Figure 17, 1kΩ Source Impedance.


Figure 18, 10kΩ Source Impedance.


Figure 19, 100kΩ Source Impedance.

The 1kΩ and 10kΩ traces show very little difference between the waveform with no series resistance while the 100kΩ trace shows a significant reduction in the channel B amplitude and an increase in the level of the noise (large jumps seen at some sample points due to incomplete settling of the ADC input). The channel B amplitude is about 88.5% lower now and a 200 mV offset has been introduced. From these tests it looks like source impedance up to 10kΩ gives acceptable results. Beyond that measurement results will start to degrade noticeably. Another set of traces for a 1MegΩ series resistor is included below as well for completeness.


Figure 20, 1MegΩ Source Impedance.

The ALICE software provides the ability to mathematically correct for gain and offset in channel B by entering correction factors (lower right corner of Scope screen. The software also has the ability to average multiple sweeps (trace averaging) to smooth out the uncorrelated noise in periodic signals. The following screen (figure 21) shows the 100kΩ results when the gain (1.13) and offset (0.2) errors for channel B are corrected and trace averaging is applied.


Figure 21, 100kΩ Source Impedance with gain / offset correction and averaging.

Negative Voltage Generator:

There are some use cases where a small negative voltage is necessary. One example is powering op-amp circuits. Many times op-amps with true rail-to-rail input and output voltage ranges such as the OP484 are not readily available. Powering a non-rail-to-rail amplifier such as the uA741 from a small negative voltage rather than ground will often be sufficient to produce a negative output swing to 0 V.

A simple switched capacitor voltage inverter, as shown in figure 22, driven by the 0 to 3.3V square wave from the PWM digital output on pin D10, can generate -2.0 volts at 1 mA of current. Diodes D1 and D2 are conventional Si diodes with 0.65 V forward drop so the peak output is reduced from 3.3 V by 2 diode drops (1.3V) to -2 V. If Schottky diodes are used the peak output voltage could be closer to -2.7 V.

Figure 22, Negative voltage generator.

Setting the digital PWM signal frequency to around 20 kHz with a 50% duty cycle is optimal. The available output current can be increased by driving capacitor C1 from higher current external CMOS drivers / gates.

As an example use case an inverting gain of 1 op-amp circuit using a uA741 is shown in figure 23. A resistor divider between GND and +3.3V generates a +1.65 V common mode voltage to bias the + input of the op-amp. A 1kΩ resistor is inserted in series with the CH B input pin to protect from possible overvoltage. This is not likely given the limited supply voltages of the uA741 but is always good practice when a test circuit is powered from supplies outside 0 to 3.3V.

Vcc (+4.7); GND; CH A AWG; 1k resistor to protect XIAO input pin; From figure 22

Figure 23, uA741 example powered from +4.7V and -2.0V.

Figure 24 shows the results. A resistor divider / attenuator is used along with Scope channel C to measure the -2.0V supply.

-2.0 V

PWM from
pin D10

GND

C1

D1
GND
+

C2

D2

10uF

0.47uF

0 to 3.3V


Figure 24, uA741 example powered from +4.7V and -2.0V.

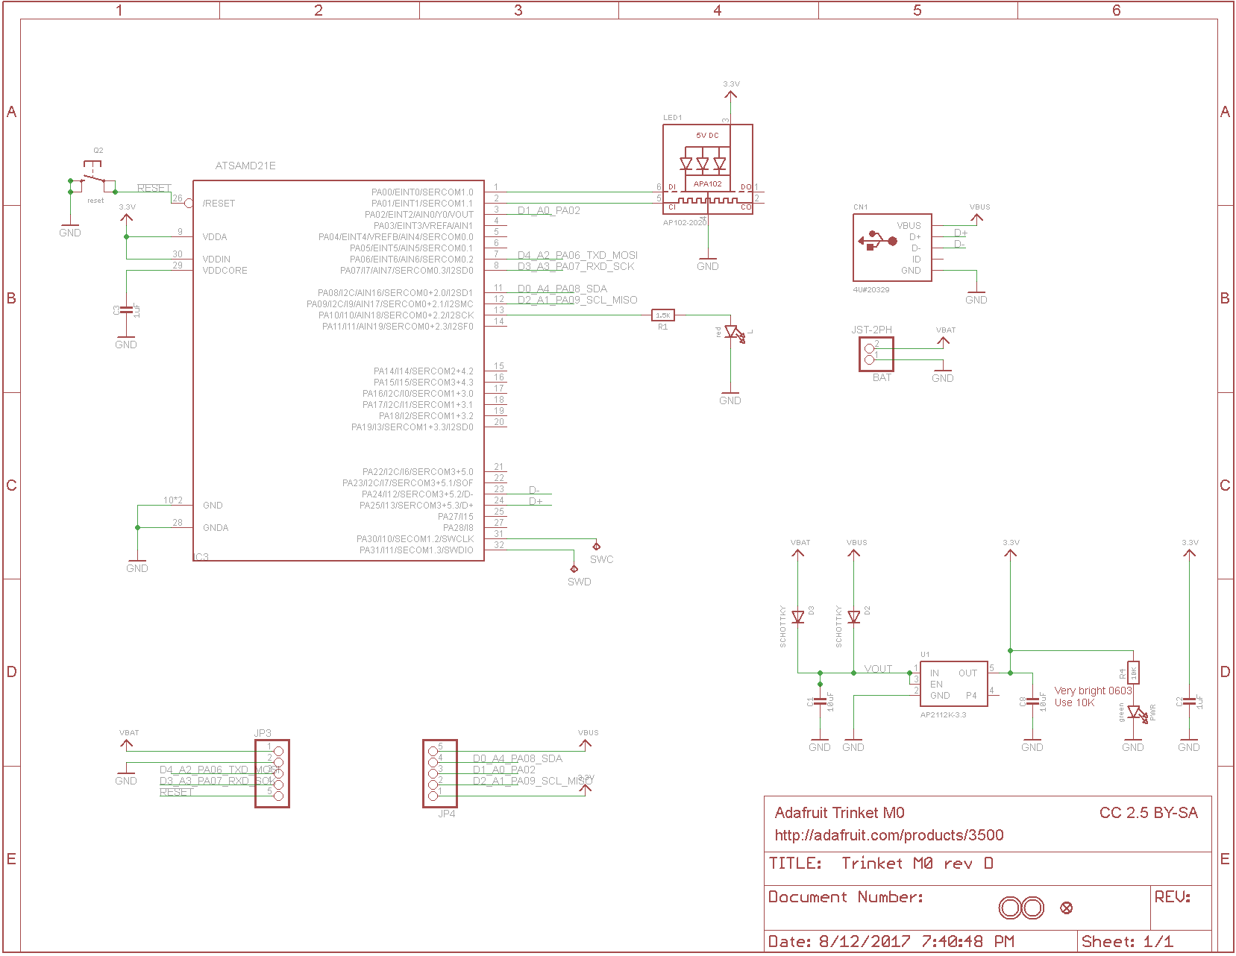
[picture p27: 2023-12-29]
Trinket_Scope_pwm_awg/trinket_m0_schem.png

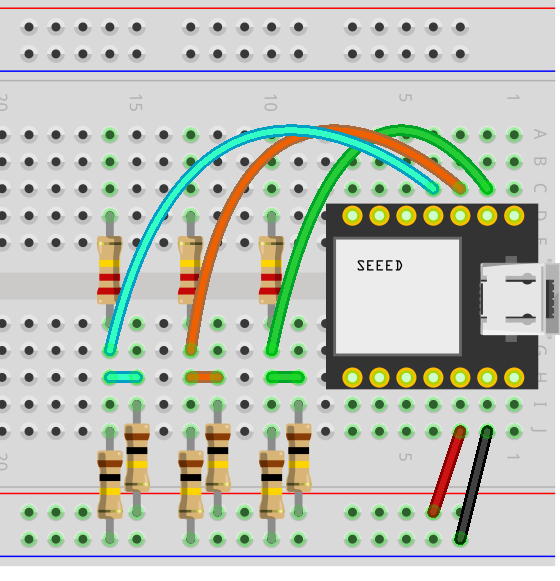
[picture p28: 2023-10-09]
XIAO/XIAO-scope-in-divider_bb.png

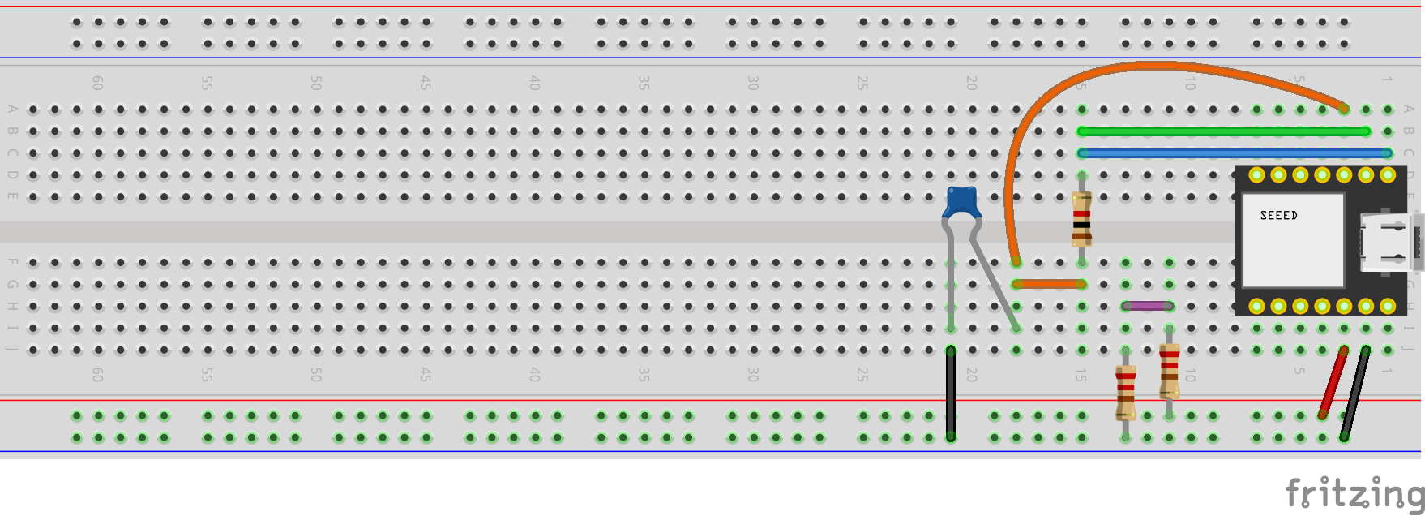
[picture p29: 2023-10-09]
XIAO/XIAO-scope-Sketch_bb.png

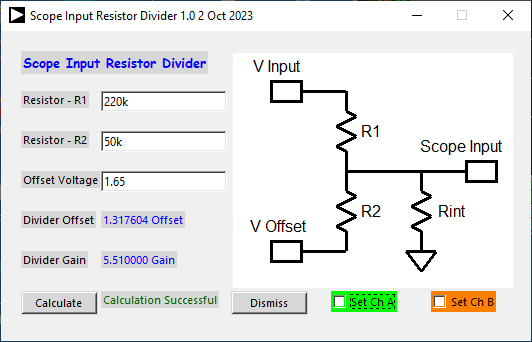
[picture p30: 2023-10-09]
XIAO/input-divider-calc.png

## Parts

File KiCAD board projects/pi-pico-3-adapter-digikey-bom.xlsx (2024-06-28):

Index | Quantity | Part Number | Manufacturer Part Number | Description | Unit Price | Extended Price USD
1 | 1 | 2648-SC0915CT-ND | SC0915 | RASPBERRY PI PICO RP2040 | 4 | 4.00
2 | 2 | S7041-ND | PPPC081LFBN-RC | CONN HDR 8POS 0.1 GOLD PCB | 0.68 | 1.36
3 | 3 | S7039-ND | PPPC061LFBN-RC | CONN HDR 6POS 0.1 GOLD PCB | 0.54 | 1.62
4 | 2 | 4610X-R2R-103LF-ND | 4610X-R2R-103LF | RES NTWRK 16 RES MULT OHM 10SIP | 0.7 | 1.40
5 | 2 | MCP6004-I/P-ND | MCP6004-I/P | IC OPAMP GP 4 CIRCUIT 14DIP | 0.59 | 1.18
6 | 3 | CF18JT910KCT-ND | CF18JT910K | RES 910K OHM 5% 1/8W AXIAL | 0.1 | 0.30
7 | 3 | CF18JT100KCT-ND | CF18JT100K | RES 100K OHM 5% 1/8W AXIAL | 0.1 | 0.30
8 | 6 | CF18JT10K0CT-ND | CF18JT10K0 | RES 10K OHM 5% 1/8W AXIAL | 0.043 | 0.43
9 | 5 | 399-13966-ND | C330C224M1R5TA | CAP CER 0.22UF 20% 100V X7R RAD | 0.33 | 1.65

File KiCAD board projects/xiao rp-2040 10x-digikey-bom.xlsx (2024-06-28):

Index | Quantity | Part Number | Manufacturer Part Number | Description | Customer Reference | Available | Backorder | Unit Price | Extended Price USD
1 | 1 | 1597-102010428-ND | 102010428 | SEEED STUDIO XIAO RP2040 ARDUINO |  | 1 | 0 | 4.68 | 4.68
2 | 2 | S7040-ND | PPPC071LFBN-RC | CONN HDR 7POS 0.1 GOLD PCB |  | 2 | 0 | 0.62 | 1.24
3 | 2 | S7039-ND | PPPC061LFBN-RC | CONN HDR 6POS 0.1 GOLD PCB |  | 2 | 0 | 0.54 | 1.08
4 | 8 | CF18JT1M00CT-ND | CF18JT1M00 | RES 1M OHM 5% 1/8W AXIAL |  | 10 | 0 | 0.043 | 0.43
5 | 8 | CF18JT100KCT-ND | CF18JT100K | RES 100K OHM 5% 1/8W AXIAL |  | 10 | 0 | 0.03 | 0.30
6 | 4 | CF18JT220RCT-ND | CF18JT220R | RES 220 OHM 5% 1/8W AXIAL |  | 10 | 0 | 0.043 | 0.43
7 | 2 | CF18JT100RCT-ND | CF18JT100R | RES 100 OHM 5% 1/8W AXIAL |  | 2 | 0 | 0.1 | 0.20
8 | 1 | MCP6004-I/P-ND | MCP6004-I/P | IC OPAMP GP 4 CIRCUIT 14DIP |  | 1 | 0 | 0.59 | 0.59
9 | 1 | MCP4922-E/P-ND | MCP4922-E/P | serial DAC |  | 1 | 0 | 3.73 | 3.73

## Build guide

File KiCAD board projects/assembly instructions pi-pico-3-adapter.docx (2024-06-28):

Assembly instructions document

This document serves as the assembly instructions for a three channel input (10X) probe adapter board for the Raspberry Pi Pico module. The adapter board scales the 0 to 3.3 V input range of the Pi Pico module by 10X and provides a means to offset the range to provide negative input voltages. An input range of +/- 16 V at the pin marked DC is the nominal configuration when the pin connected to the 100kΩ of the input divider is connected to VCM (1.65V). Other input divider configurations are possible. The board also contains two R/2R SIP resistor arrays that provide two 8 bit DAC AWG output channels.

These instructions do not teach the reader how to solder through-hole printed circuit boards. We could reproduce a soldering tutorial here but seriously, there are so many good ones out there already, it's probably a waste of time. If the reader has little experience soldering then the following tutorials from SparkFun may be useful:

https://www.sparkfun.com/tutorials/106

https://learn.sparkfun.com/tutorials/how-to-solder-through-hole-soldering

Other such soldering tutorials may be found on line as well.

The Pi Pico board has castellated mounting holes and the following tutorial may be of help when mounting the Pi Pico:

https://learn.sparkfun.com/tutorials/how-to-solder-castellated-mounting-holes

Bill of Materials:

Item | Qty | Reference(s) | Value
1 | 5 | C1, C2, C3, C4, C7 | 0.22u
2 | 2 | C5, C6 | 1n
3 | 1 | J1 | One 1X16 or Two 1X8 Female Header
4 | 1 | J3 | 1X8 Female Header
5 | 1 | J4 | 1X8 Female Header
6 | 7 | R1, R2, R3, R4, R5, R6, R7 | 510
7 | 6 | R8, R9, R10, R11, R18, R19 | 10k (CF18JT10K0CT-ND)
8 | 3 | R12, R14, R16 | 100k (CF18JT100KCT-ND)
9 | 3 | R13, R15, R17 | 910k (CF18JT910KCT-ND)
10 | 2 | RDACA1, RDACB1 | R-2R 10k (4610X-R2R-103LF)
11 | 2 | U1, U2 | LM324 or MCP6004
12 | 1 | U3 | Pi Pico (2648-SC0915CT-ND)

Amplifiers U1 and U2 use the standard pinout for quad op-amps and any version that can operate from a 4.7 V power supply could potentially be used. Rail-Rail input / output capable amplifiers are best suited for this application. Low cost quad devices such as the LM324 or similar can be used because it supports an input common mode voltage that includes ground. Depending on the particular version / vendor of the LM324, pull down resistors R1, R2, R3, R4, R5, R6, R7 (510 ohm) may or may not be needed. If a true Rail-Rail amplifier such as the MCP6004 is used resistors R1, R2, R3, R4, R5, R6, R7 can be omitted.

It is best to start assembly with the components with the lowest profile, like the resistors. Place all the resistors of the same value at a time and solder them in place before moving on to the next value. Locate where each resistor goes by the reference designator (R1, R2 etc.) on the silk screen (Note: figure 2.) A small piece of masking tape can be used to hold the resistors tight to the top surface of the board while soldering the leads on the bottom of the board. Once all the resistors are installed move on to the next highest profile components like the DIP op-amp. Be sure to note the notch in the silk screen outline for the op-amp and Pin 1 designated by the square solder pad. Be sure to insert the op-amp properly aligned with Pin 1.

The Pi Pico board can be installed directly on the SMD pads using the U3 location with the USB connector facing outward toward the PCB board edge (Note: figure 3 assembled PCB).

The female header sockets are the tallest and should be installed last.

Schematic and board layout for 4/26/2024 Prototype:

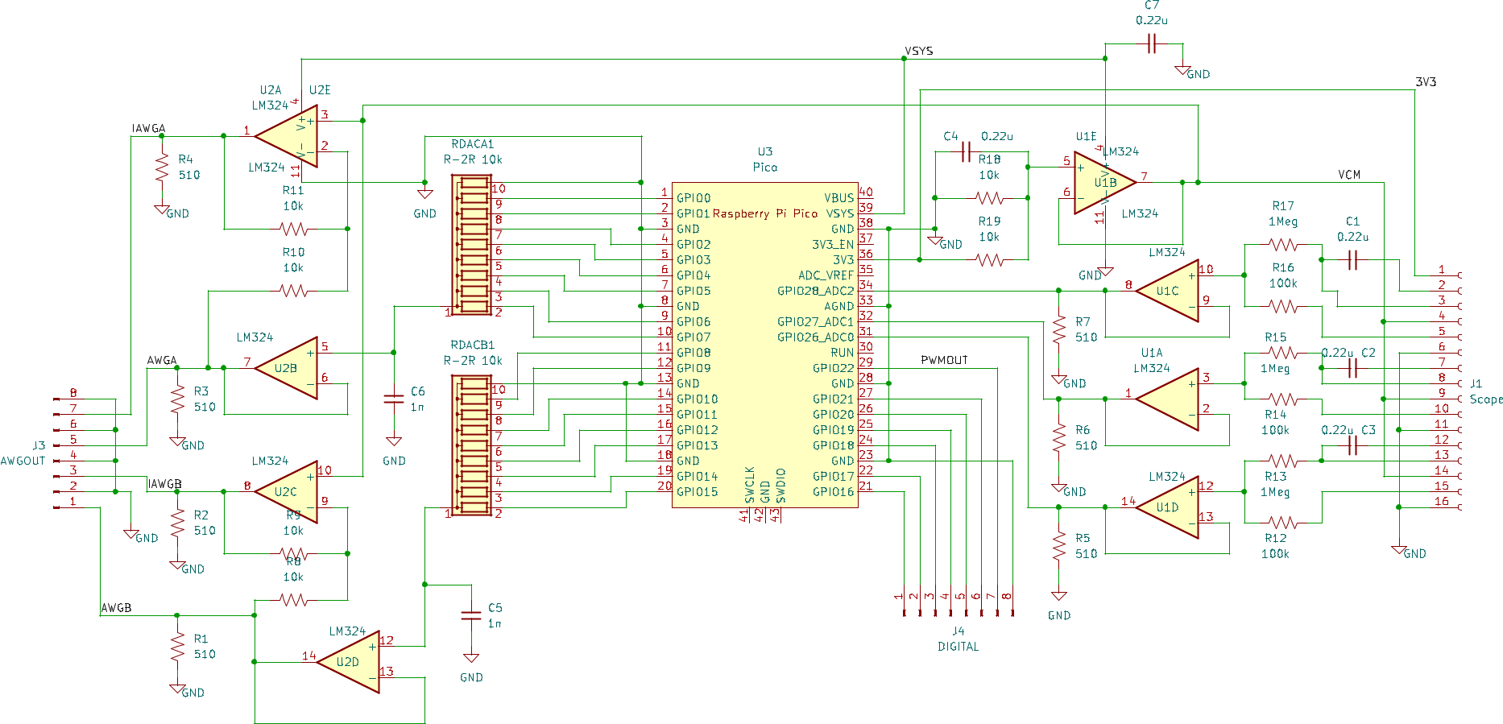
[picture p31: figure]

Figure 1 Raspberry Pi Pico 10X probe schematic (prototype)

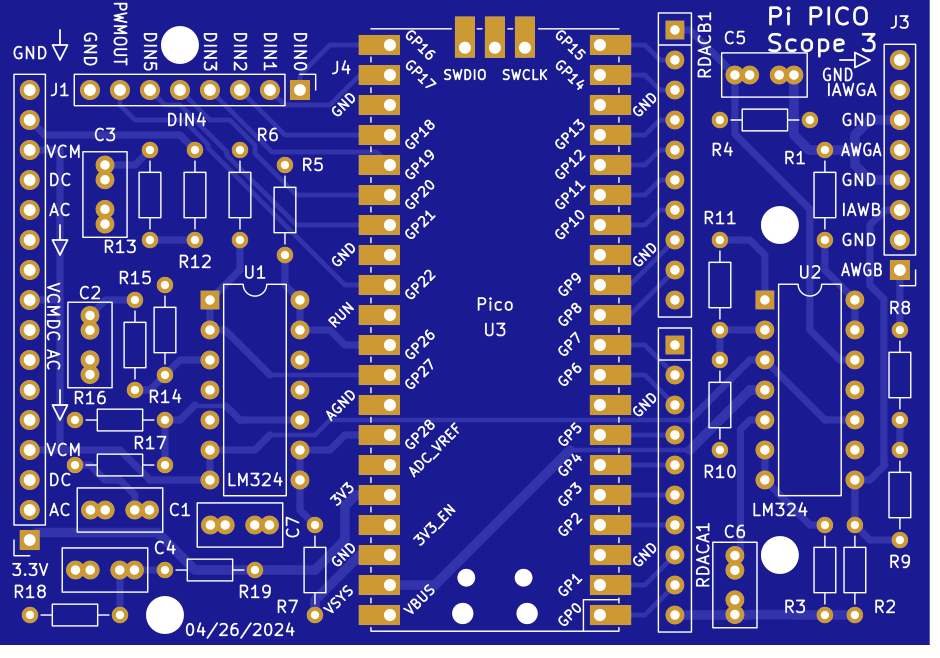
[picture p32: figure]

Figure 2 Raspberry Pi Pico 10X probe PCB Top - silk screen (prototype)

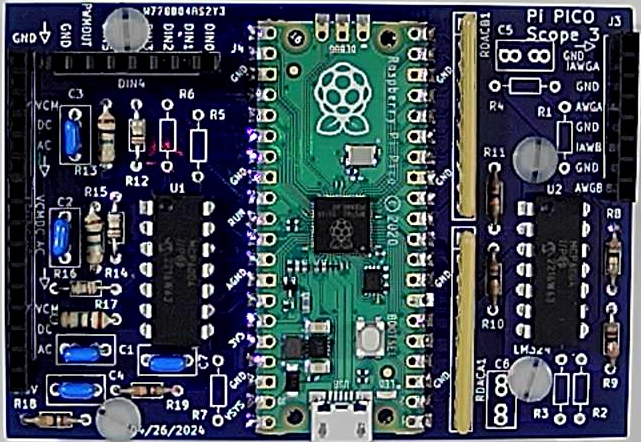
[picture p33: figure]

Figure 3 Raspberry Pi Pico 10X probe PCB (prototype) assembled (MCP6004).

Resistor Color Code:

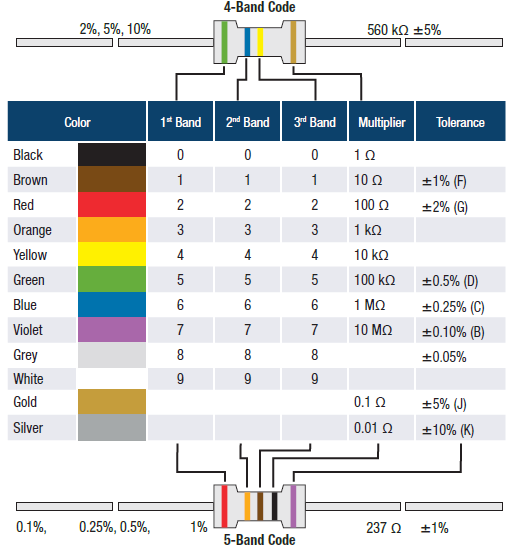
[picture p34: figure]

Soldering Hints:

1. Insert the component tight against the PCB surface and carefully solder the leads.

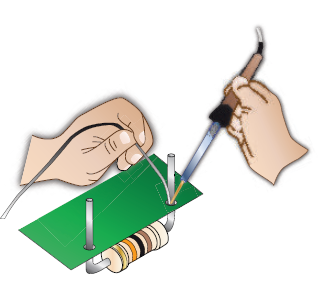
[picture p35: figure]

2. Make sure the solder joints completely surround the component lead and are cone-shaped and shiny.

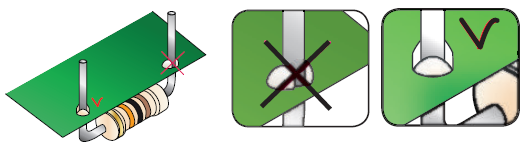
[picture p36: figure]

3. Trim excess leads as close as possible to the solder joint.

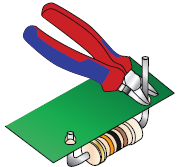
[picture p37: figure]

Appendix for Version 3 Layout (5/11/2024):

The version 3 design is electrically identical to the prototype. The physical arrangement of the components was changed to make more sense.

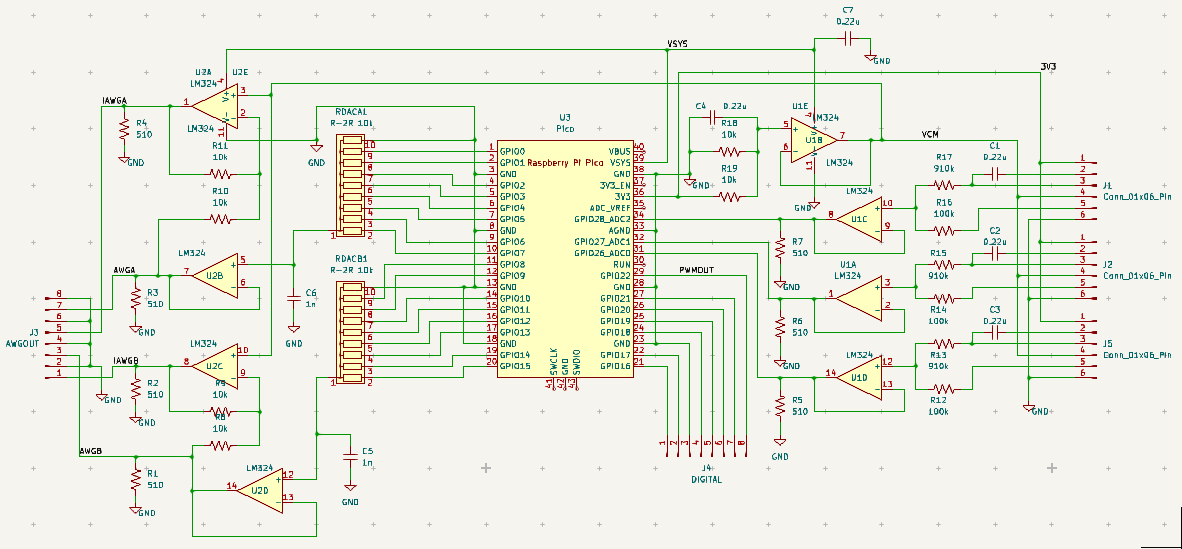
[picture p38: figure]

Version 3 schematic

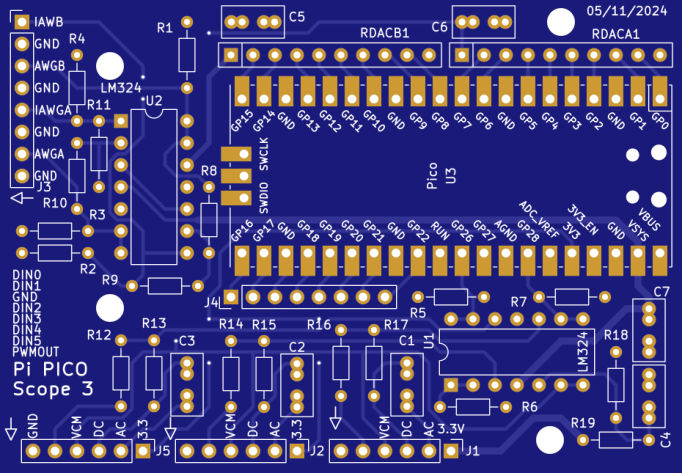
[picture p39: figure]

Version 3 Top Silk screen

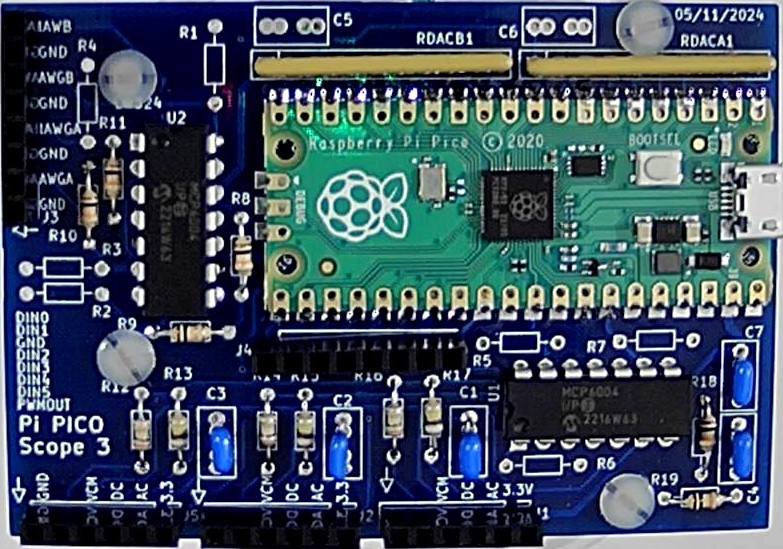
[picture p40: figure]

Assembled Version 3

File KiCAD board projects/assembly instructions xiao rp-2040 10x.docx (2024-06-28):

Assembly instructions document

This document serves as the assembly instructions for a four channel differential input 10X probe adapter board for XIAO RP-2040 module. The adapter board scales the 0 to 3.3 V input range of the XIAO module by 10X and provides a means to offset the range to provide negative input voltages. +/- 16 V differential input is the nominal configuration. The board also contains a MCP two channel serial DAC to provide two AWG output channels.

These instructions do not teach the reader how to solder through-hole printed circuit boards. We could reproduce a soldering tutorial here but seriously, there are so many good ones out there already, it's probably a waste of time. If the reader has little experience soldering then the following tutorials from SparkFun may be useful:

https://www.sparkfun.com/tutorials/106

https://learn.sparkfun.com/tutorials/how-to-solder-through-hole-soldering

Other such soldering tutorials may be found on line as well.

Bill of Materials:

Item | Qty | Reference(s) | Value
1 | 2 | C1, C2 | C
2 | 2 | J1, J2 | 01x06 Female Header Pin
3 | 2 | J5, J6 | XIAO RP-2040 Board
4 | 1 | J4 | 01x07 Female Header Pin
5 | 8 | R1, R2, R3, R4, R5, R6, R7, R8 | 1Meg
6 | 8 | R9, R10, R11, R12, R13, R14, R15, R16 | 100k
7 | 2 | R17, R18 | 100
8 | 4 | R19, R20, R21, R22 | 220
9 | 4 | R23, R24, R25, R26 | 510
10 | 2 | R27, R28 | 1k
11 | 1 | RV1 | 500
12 | 1 | U1 | LM324 or LM2902 or MCP6004
13 | 1 | U2 | MCP4922

Amplifier U1 uses the standard pinout for quad op-amps and any version that can operate from a 4.7 V power supply could potentially be used. Rail-Rail input / output capable amplifiers are best suited for this application. Low cost quad devices such as the LM324 or similar can be used because it supports an input common mode voltage that includes ground. Depending on the particular version / vendor of the LM324, pull down resistors R23 – R26 (510 ohm) may or may not be needed. If a true Rail-Rail amplifier such as the MCP6004 is used resistors R23, R24, R25, R26 can be omitted.

It is best to start assembly with the components with the lowest profile, like the resistors. Place all the resistors of the same value at a time and solder them in place before moving on to the next value. Locate where each resistor goes by the reference designator (R1, R2 etc.) on the silk screen (Note: figure 2.) A small piece of masking tape can be used to hold the resistors tight to the top surface of the board while soldering the leads on the bottom of the board. Once all the resistors are installed move on to the next highest profile components like the DIP op-amp. Be sure to note the notch in the silk screen outline for the op-amp and Pin 1 designated by the square solder pad. Be sure to insert the op-amp properly aligned with Pin 1.

The XIAO RP-2040 board is installed using the J5 and J6 locations with the USB C connector facing outward toward the PCB board edge (Note: figure 3 assembled PCB).

The female header sockets are the tallest and should be installed last.

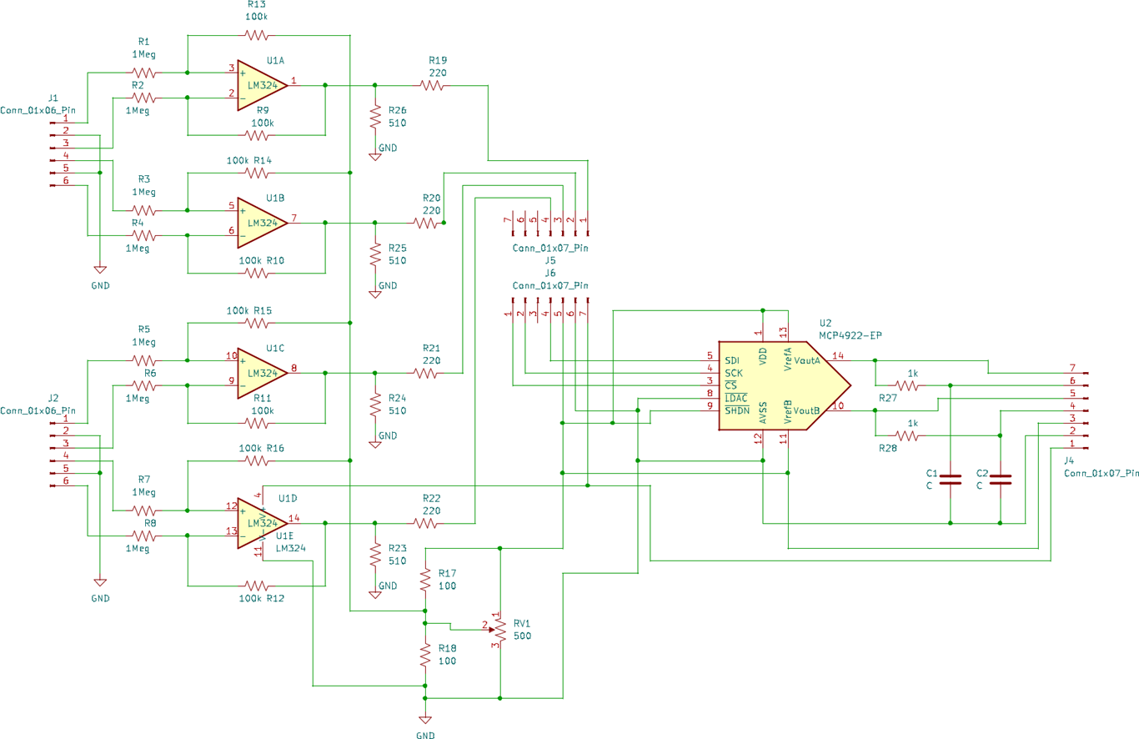
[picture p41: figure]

Figure 1 XIAO RP-2040 10X probe schematic

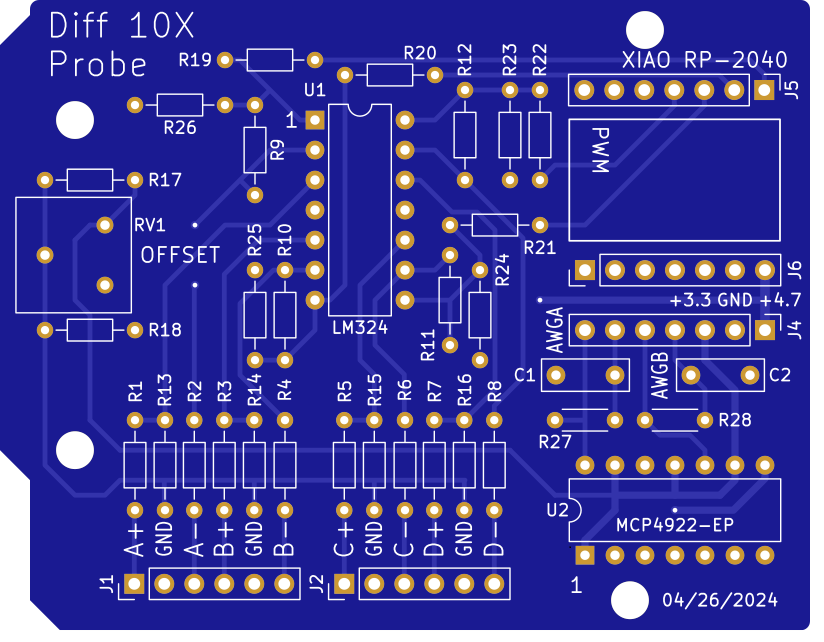
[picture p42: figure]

Figure 2 XIAO RP-2040 10X probe PCB Top - silk screen

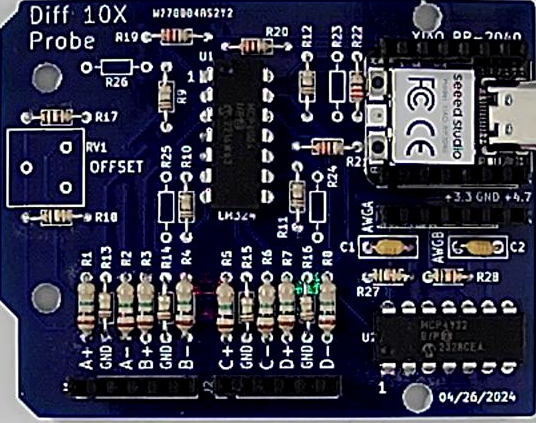
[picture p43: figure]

Figure 3 XIAO RP-2040 10X probe PCB assembled (MCP6004).

Resistor Color Code:


Soldering Hints:

1. Insert the component tight against the PCB surface and carefully solder the leads.


2. Make sure the solder joints completely surround the component lead and are cone-shaped and shiny.


3. Trim excess leads as close as possible to the solder joint.


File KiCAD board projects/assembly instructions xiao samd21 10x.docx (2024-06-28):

Assembly instructions document

This document serves as the assembly instructions for a four channel differential input 10X probe adapter board for the XIAO SAMD21 module. The adapter board scales the 0 to 3.3 V input range of the XIAO module by 10X and provides a means to offset the range to provide negative input voltages. +/- 16 V differential input is the nominal configuration.

These instructions do not teach the reader how to solder through-hole printed circuit boards. We could reproduce a soldering tutorial here but seriously, there are so many good ones out there already, it's probably a waste of time. If the reader has little experience soldering then the following tutorials from SparkFun may be useful:

https://www.sparkfun.com/tutorials/106

https://learn.sparkfun.com/tutorials/how-to-solder-through-hole-soldering

Other such soldering tutorials may be found on line as well.

Bill of Materials:

Item | Qty | Reference(s) | Value
1 | 2 | J1, J2 | 01x06 Female Header Pin
2 | 2 | J3, J4 | 01x07 Female Header Pin
3 | 1 | J5, J6 | XIAO SAMD21 Board
4 | 8 | R1, R2, R3, R4, R5, R6, R7, R8 | 1Meg (1/8W)
5 | 8 | R9, R10, R11, R12, R13, R14, R15, R16 | 100k (1/8W)
6 | 2 | R17, R18 | 100 (1/8W)
7 | 4 | R19, R20, R21, R22 | 220 (1/8W)
8 | 4 | R23, R24, R25, R26 | 510 (1/8W)
9 | 1 | RV1 | 500 (optional)
10 | 1 | U1 | LM324 or LM2902 or MCP6004

Amplifier U1 uses the standard pinout for quad op-amps and any version that can operate from a 4.7 V power supply could potentially be used. Rail-Rail input / output capable amplifiers are best suited for this application. Low cost quad devices such as the LM324 or similar can be used because it supports an input common mode voltage that includes ground. Depending on the particular version / vendor of the LM324, pull down resistors R23 – R26 (510 ohm) may or may not be needed. If a true Rail-Rail amplifier such as the MCP6004 is used resistors R23, R24, R25, R26 can be omitted.

It is best to start assembly with the components with the lowest profile, like the resistors. Place all the resistors of the same value at a time and solder them in place before moving on to the next value. Locate where each resistor goes by the reference designator (R1, R2 etc.) on the silk screen (Note: figure 2.) A small piece of masking tape can be used to hold the resistors tight to the top surface of the board while soldering the leads on the bottom of the board. Once all the resistors are installed move on to the next highest profile components like the DIP op-amp. Be sure to note the notch in the silk screen outline for the op-amp and Pin 1 designated by the square solder pad. Be sure to insert the op-amp properly aligned with Pin 1.

The XIAO SAMD21 board is installed using the J5 and J6 locations with the USB C connector facing outward toward the PCB board edge (Note: figure 3 assembled PCB).

The female header sockets are the tallest and should be installed last.

The offset adjustment pot, RV1, is optional. If a 250 Ω pot is used you should increase R17, R18 to 220 Ω or even leave them off for a lower value RV1.

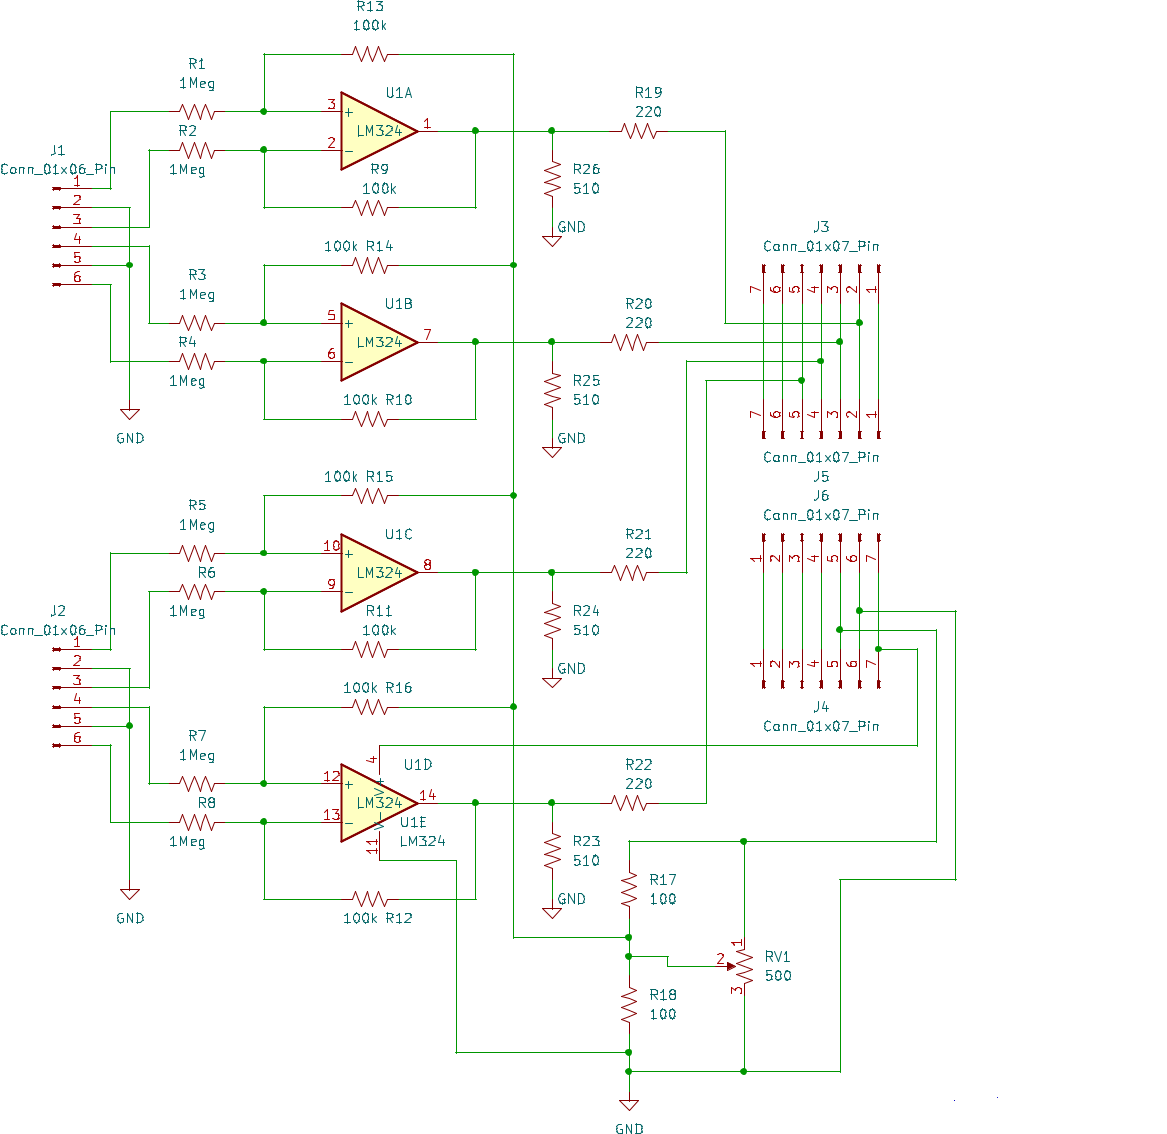
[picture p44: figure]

Figure 1 XIAO SAMD21 10X probe schematic

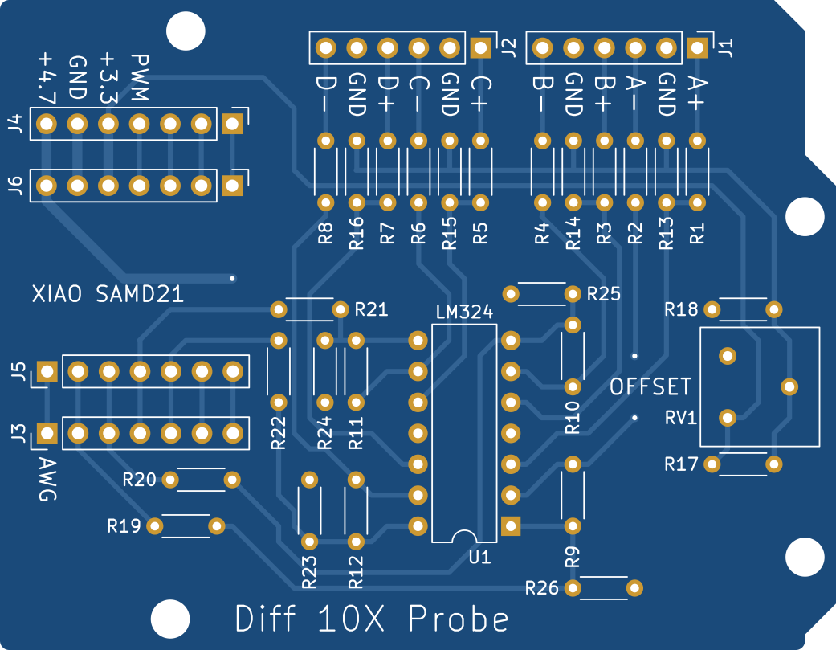
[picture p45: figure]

Figure 2 XIAO SAMD21 10X probe PCB Top - silk screen

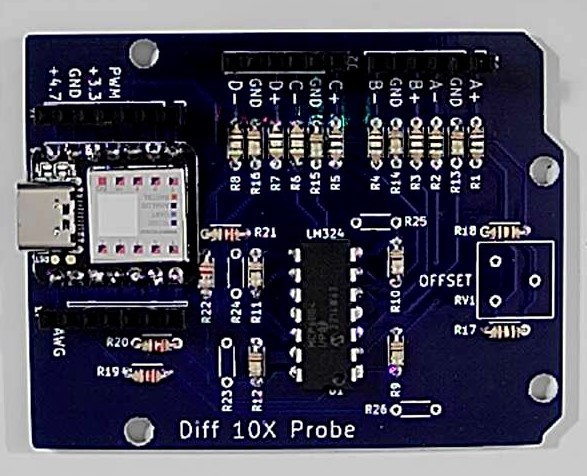
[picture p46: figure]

Figure 3 XIAO SAMD21 10X probe PCB assembled (MCP6004).

Resistor Color Code:


Soldering Hints:

1. Insert the component tight against the PCB surface and carefully solder the leads.


2. Make sure the solder joints completely surround the component lead and are cone-shaped and shiny.


3. Trim excess leads as close as possible to the solder joint.


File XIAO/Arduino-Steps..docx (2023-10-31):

An ordered list of steps to program Seeed Studio XIAO SAMD21:

First: Download Arduino IDE for your computer operating system from here: https://www.arduino.cc/en/software

Second: Run the installer software you just down loaded.

Third: Run the Arduino IDE by double clicking on the newly installed desktop icon.

Under Files click on Open and open the XIAO_Scope_pwm_awg.ino file you down loaded from here:

https://github.com/damercer/Arduino-Scopes/blob/main/XIAO/XIAO_Scope_pwm_awg/XIAO_Scope_pwm_awg.ino

Alternately when you installed Arduino it should have connected the .ino file extension with Arduino and double clicking on the .ino file should open it in the Arduino IDE.

Arduino will probably throw up a message about the file needing to be in a folder by itself. Just click OK and it will move the file for you. You should see the source code now.

Fourth: Under File > Click on Preferences. Should see below.

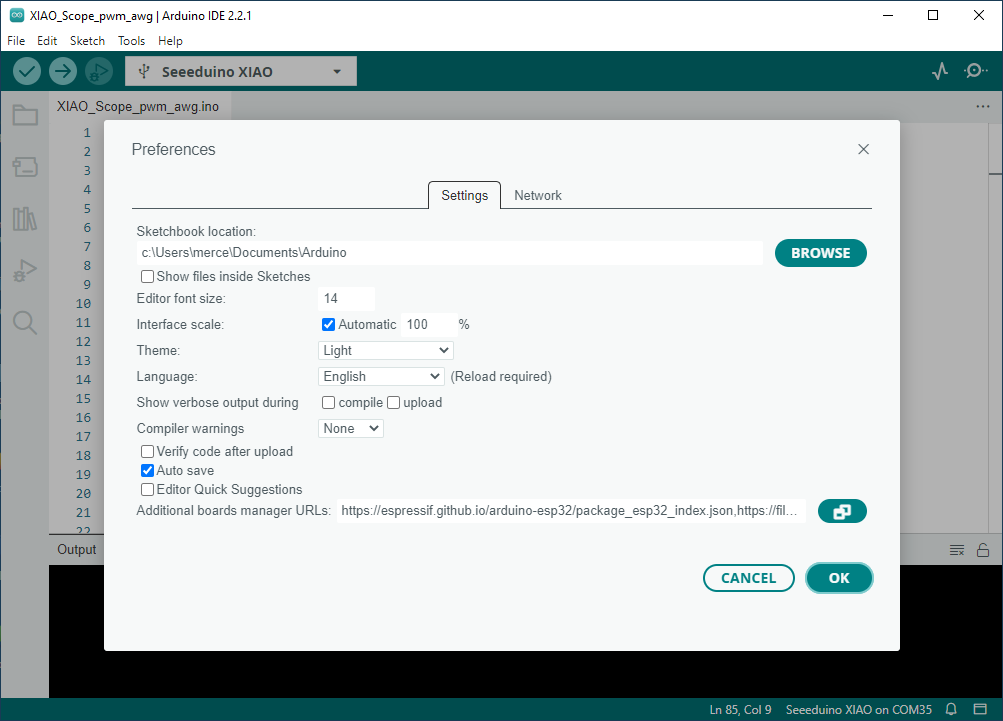
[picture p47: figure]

Click on the blue button to the right of the line Additional boards manager URLs: Below should appear.

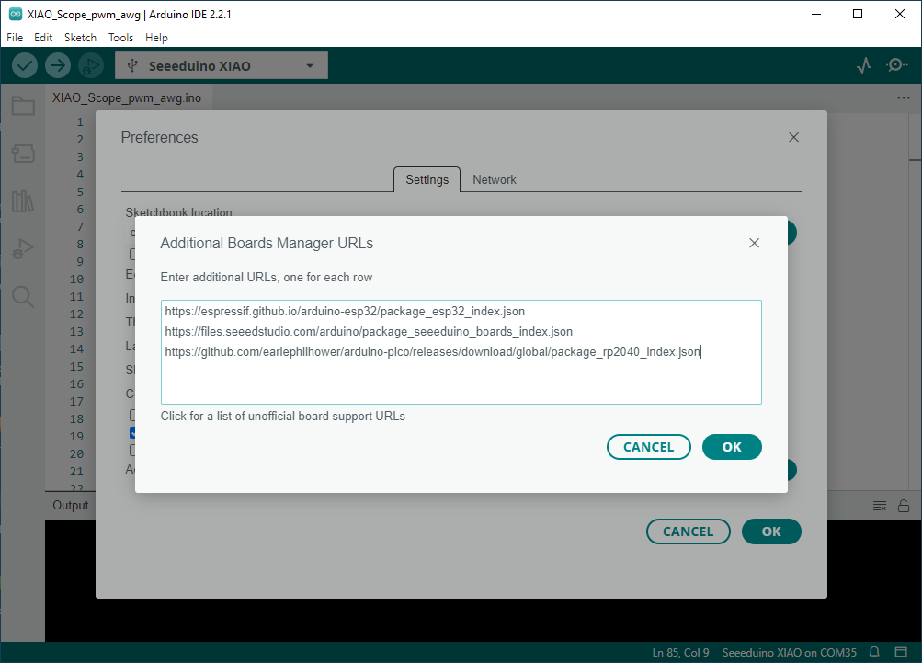
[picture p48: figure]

The above is from software which already has this step done so... Copy and paste the following into the edit window and click OK.

https://files.seeedstudio.com/arduino/package_seeeduino_boards_index.json

Once the link to the Seeed Studio package has been added to the above list it still needs to be installed for the SAMD21 board. Open the Boards Manager and type XIAO in the Search bar. Scroll down until you see the Seeed SAMD Boards listed. Click on Install. Should look like the following:

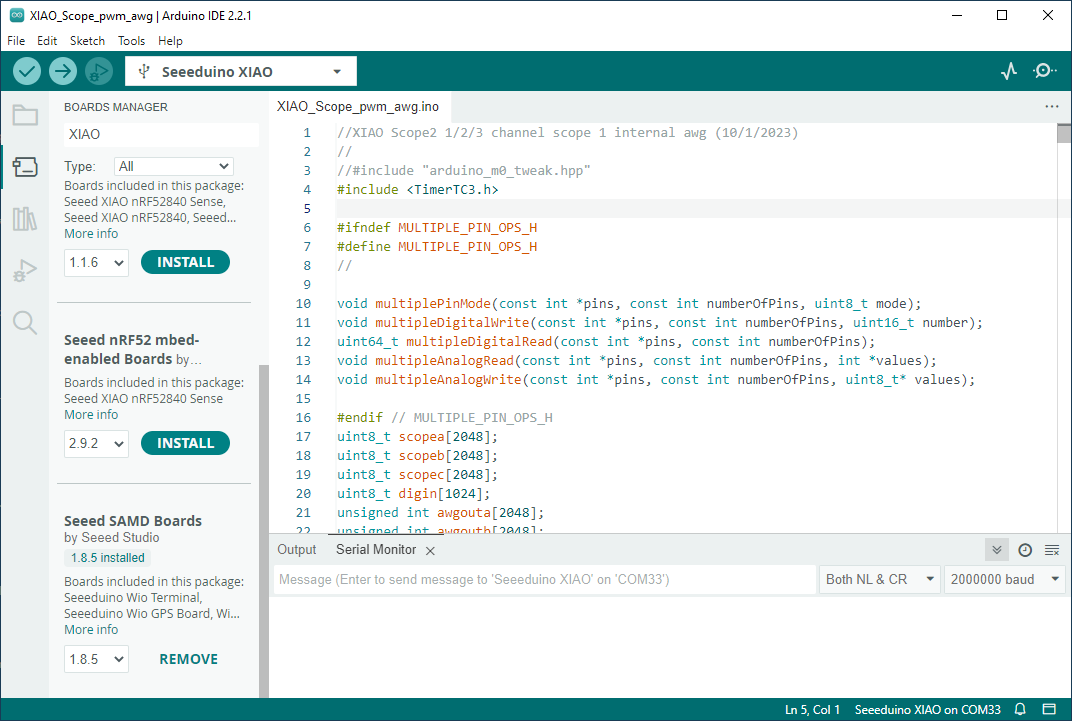
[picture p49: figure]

Fifth: with the XIAO board plugged into a USB port click on Tools > Board > Board Manager. Should see something like below. But again this is from a version with this step already done. For you there won't be anything next to Board: because you have not selected one yet. You should be able to find the correct one in the list as shown below.

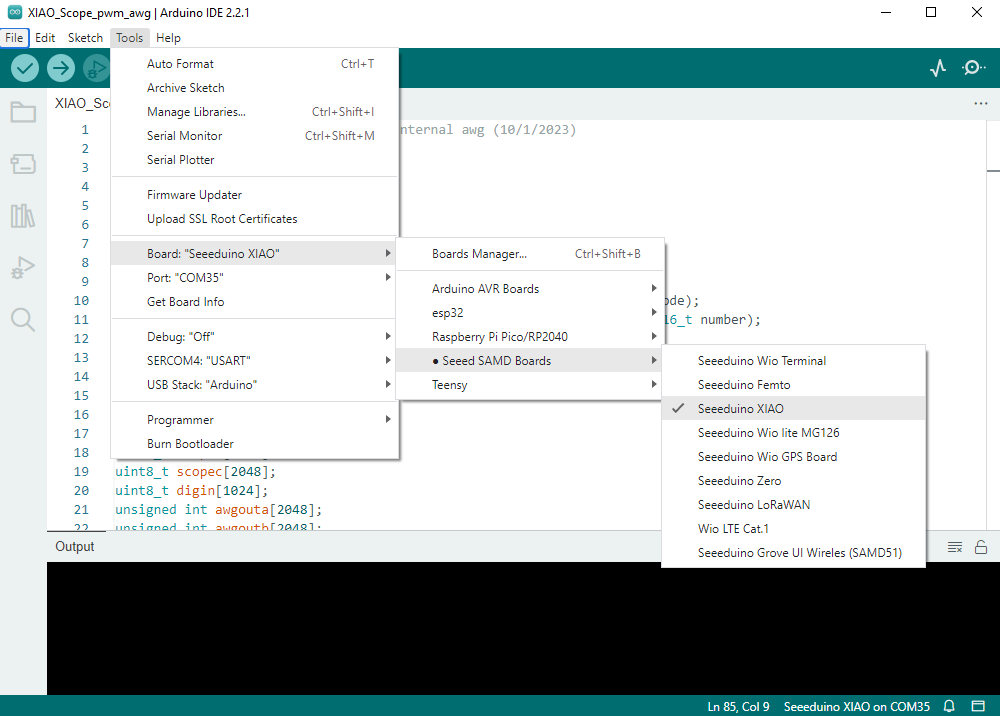
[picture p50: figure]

Sixth:

Click on Tools > Ports and select the correct COM port for the board. Again your COM port number may be different, should be some number larger than 3 or 4 depending on how many other USB devices you might have used in the past.

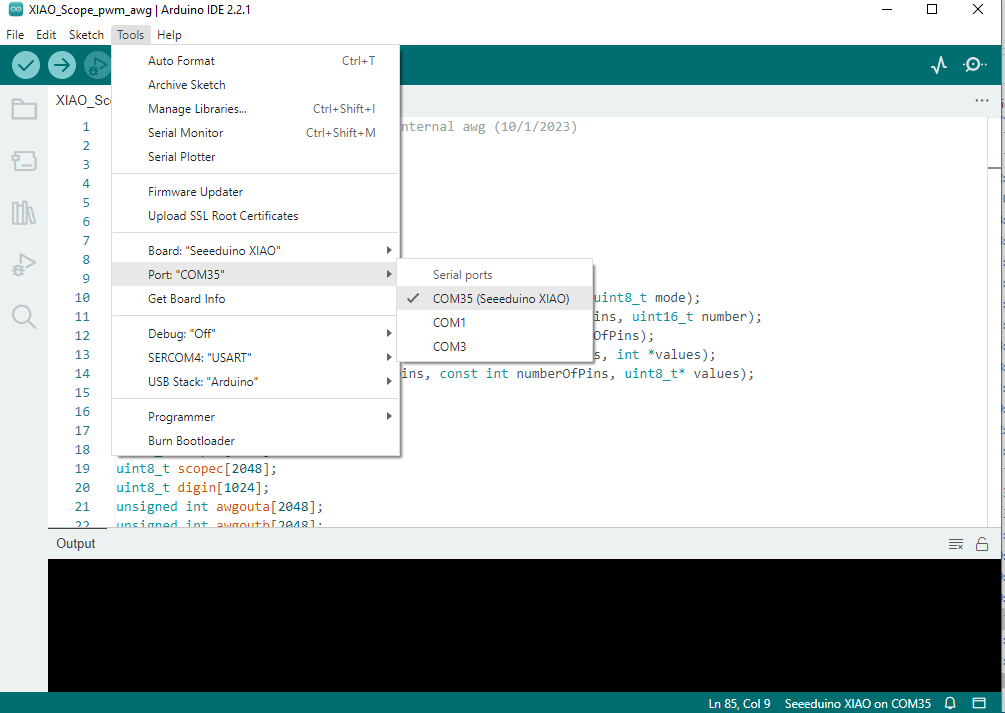
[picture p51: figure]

On the bottom of the screen you should see an indication like: Seeeduino XIAO on COMXX.

Seventh: Click on the Right pointing Arrow to compile and up load the software to the board.

The XIAO SAMD21 board should now be programed to work with Universal ALICE GUI.

There is one additional "test" step (not necessary to continue) that is useful to confirm that the software on the board is functioning. Again you don't need to do this step.

In the Arduino IDE in the upper right there a two small icons, one that looks like a squiggle and one that looks like a circle with a dot. The circle with a dot one opens the Serial Monitor which is used to help debug operation and to communicate with the board. Open the Serial Monitor. A place to enter test will appear near the middle of the screen under where the source code is. Type a capital I and type enter. The board should respond with the ID string "XIAO Scope 3.0". This will confirm that the code is loaded and running

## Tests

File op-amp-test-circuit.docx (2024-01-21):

Four Transistor Op-Amp Test Circuit

Objective:

This is a simple transistor Op-Amp test circuit to demonstrate lab testing using the XIAO SAMD21 based measurement module with ALICE Universal in hands on circuits and electronics labs.

The XIAO Based measurement module:

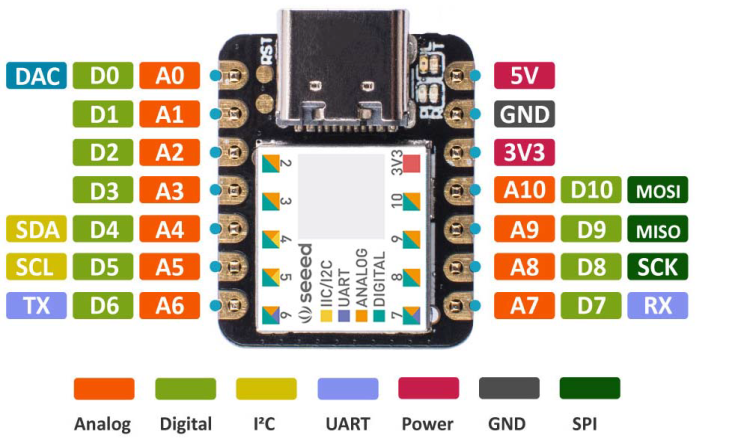
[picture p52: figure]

AWG Output

Scope CH A

Scope CH B

Scope CH C

Power Supplies and Ground

The circuit:

A simple three stage op-amp can be constructed using just four bipolar transistors, 12 resistors and 1 capacitor. The LTspice simulation schematic is shown in figure 1. The differential input stage consists of NPN transistors Q1 and Q2, emitter tail resistor R1 and collector load resistors R2, R3. A resistor degenerated common emitter PNP second stage consists of Q4, R4 and R5. Miller compensation capacitor C1 insures stability and sets the amplifier slew rate. A final emitter follower output stage consists of NPN Q3 and resistor R6.

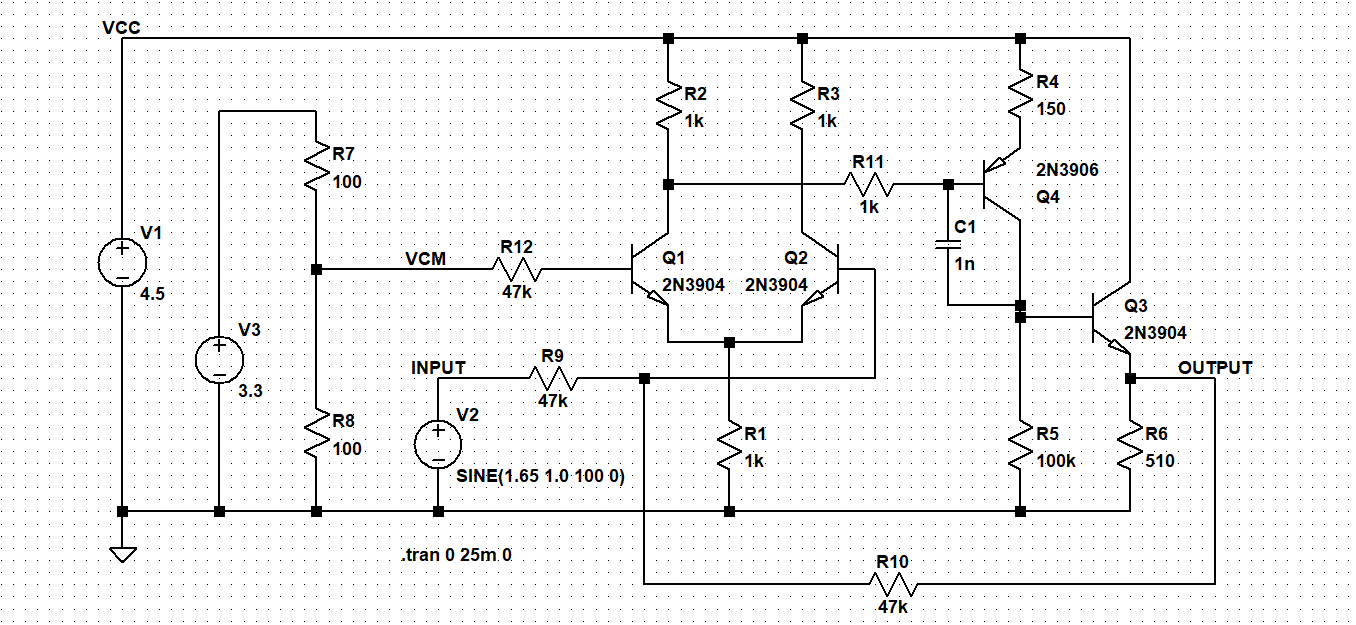
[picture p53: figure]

Figure 1, LTspice schematic

A resistor divider across the 3.3V power supply, R7 and R8, generates a 1.65 V common mode voltage VCM at the + input (base of Q1). The amplifier is configured as an inverter with a gain of -1 with feedback resistors R9 and R10 connected to the – input (base of Q2).

LTspice simulation results are shown in figure 2.

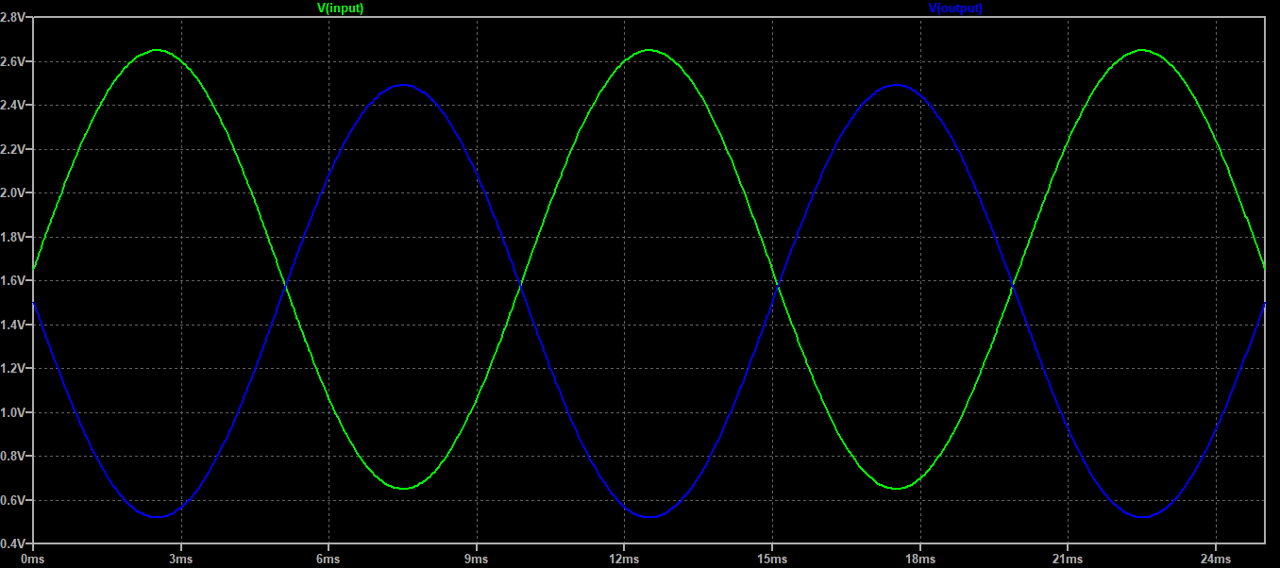
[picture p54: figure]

Figure 2, LTspice simulation results

Construction:

The circuit can be constructed on a solderless breadboard alongside the XIAO SAMD21 measurement module as shown in figure 3. The two bottom rails are connected to GND and 3.3V from the module and the top (red) rail is connected to the approximately 4.5 V supplied from the USB port minus 1 diode drop.

The AWG output and the Channel A scope input are tied together and is the input to the amplifier. The Channel B scope input measures the amplifier output.

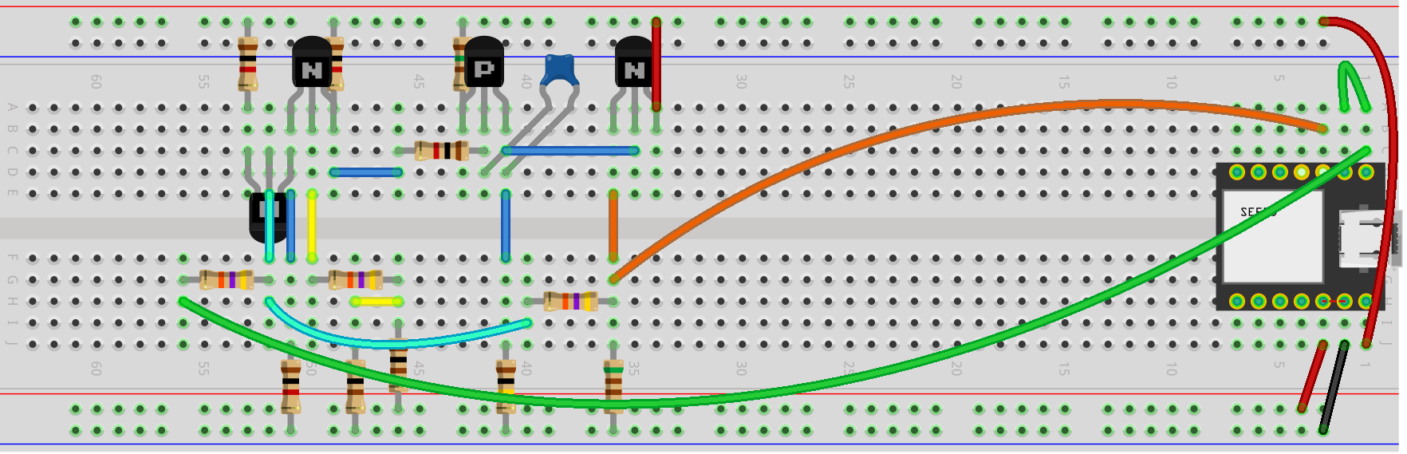
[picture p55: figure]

Figure 3, Solderless Breadboard Layout

Care should be taken to insure that the Scope inputs are never connected to voltages greater than 3.3 V such as the 4.5 V rail used here to power the circuit. The Scope inputs can be made “5V Tolerant” by inserting a resistor of at least 5kΩ (4.7kΩ or 5.1kΩ) between the XIAO module pin and the circuit node being measured. The added series resistance will have a negligible effect owing to the very high impedance of the ADC inputs but limit the current to a safe level.

The amplifier output should never exceed the 3.3 V maximum output of the AWG when configured as in this example. Increasing the gain by changing the feedback resistors could cause the output to exceed 3.3 V.

Measurement Results:

The ALICE user interface is used in conjunction with the module to drive and measure the test circuit. The screen shot in figure 4 shows similar results to the LTspice simulation.

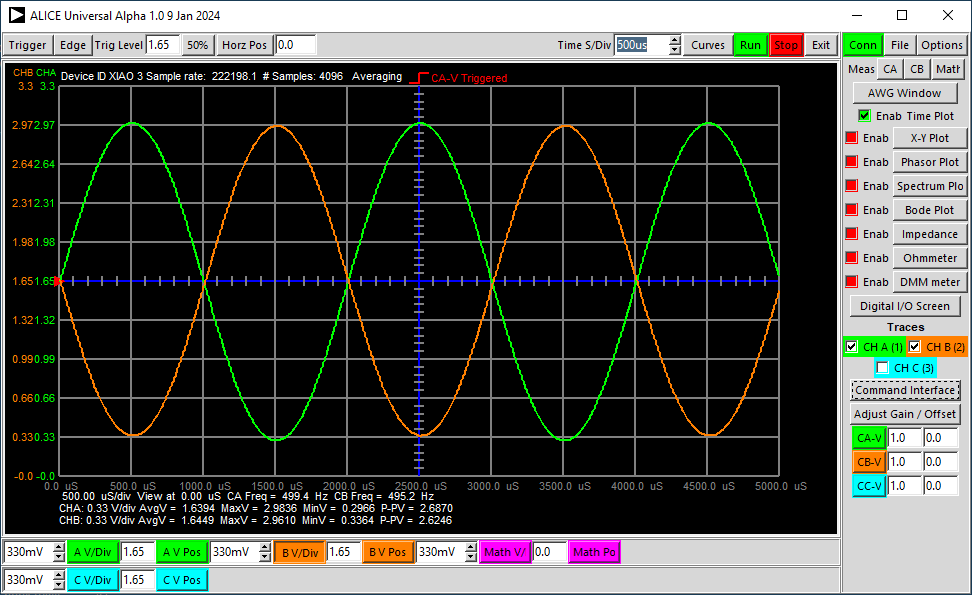
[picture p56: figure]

Figure 4, ALICE Scope screen.

If we increase the value of the compensation capacitor C1 to 10 nF and switch the AWG waveform shape to a square wave we can measure the resulting slew rate. We can also turn on and connect scope Channel C to the summing junction at the – input of the amplifier to view the input voltage difference seen when the amplifier is slewing as shown in figure 5.

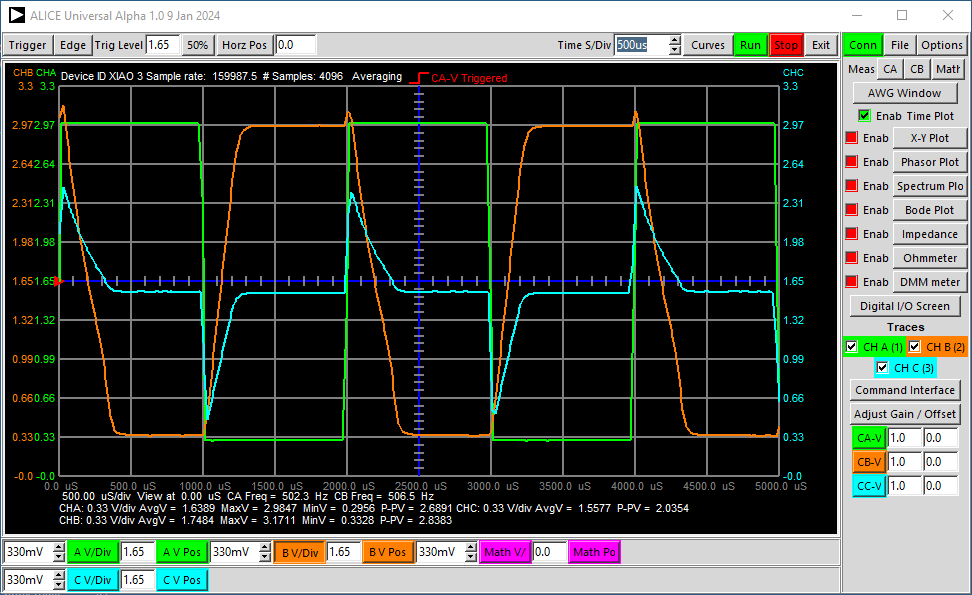
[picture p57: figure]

Figure 5, Slew rate test.

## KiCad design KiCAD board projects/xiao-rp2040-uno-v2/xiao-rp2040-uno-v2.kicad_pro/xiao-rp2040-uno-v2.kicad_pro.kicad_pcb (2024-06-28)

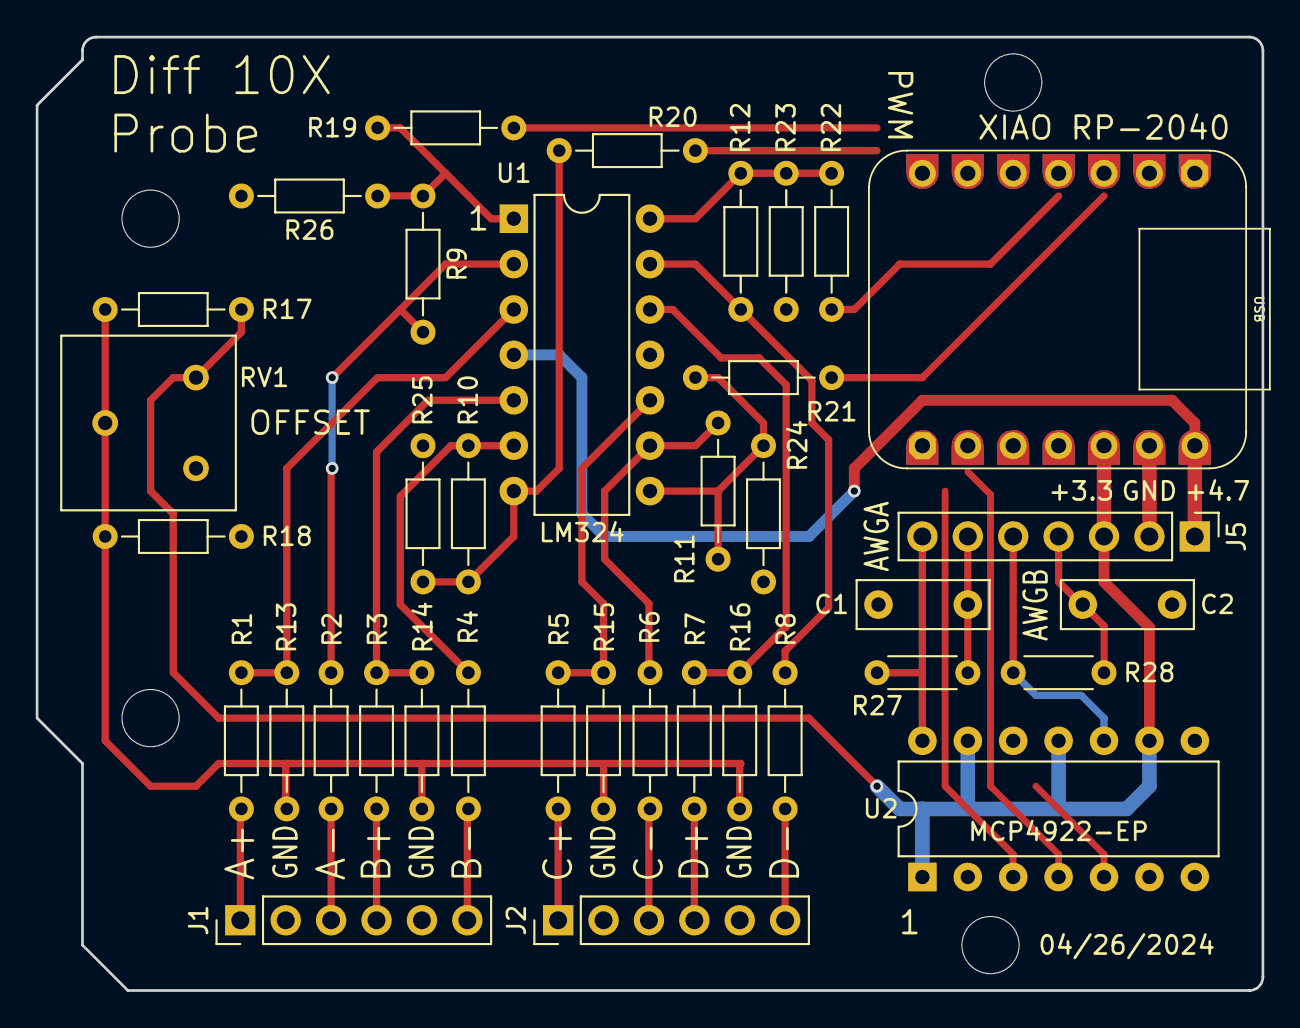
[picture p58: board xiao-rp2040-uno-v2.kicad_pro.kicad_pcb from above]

Board: 6 copper layers, 68.6 x 53.3 mm, 42 parts (0 on the bottom side), 35 nets.

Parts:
C1, C2: C; C_Rect_L7.2mm_W2.5mm_P5.00mm_FKS2_FKP2_MKS2_MKP2
J1, J2: Conn_01x06_Pin; PinHeader_1x06_P2.54mm_Vertical
J2#2, J4: DNP; H7-HALF-HOLE-2.54
J5: Conn_01x07_Pin; PinHeader_1x07_P2.54mm_Vertical
MH1, MH2, MH3, MH4: MountingHole_3.2mm
R1, R2, R3, R4, R5, R6, R7, R8: 1Meg; R_Axial_DIN0204_L3.6mm_D1.6mm_P7.62mm_Horizontal
R9, R10, R11, R12, R13, R14, R15, R16: 100k; R_Axial_DIN0204_L3.6mm_D1.6mm_P7.62mm_Horizontal
R17, R18: 100; R_Axial_DIN0204_L3.6mm_D1.6mm_P7.62mm_Horizontal
R19, R20, R21, R22: 220; R_Axial_DIN0204_L3.6mm_D1.6mm_P7.62mm_Horizontal
R23, R24, R25, R26: 510; R_Axial_DIN0204_L3.6mm_D1.6mm_P7.62mm_Horizontal
R27, R28: 1k; R_Axial_DIN0204_L3.6mm_D1.6mm_P5.08mm_Horizontal
RV1: 500; Potentiometer_Bourns_3386F_Vertical
U1: LM324; DIP-14_W7.62mm
U2: MCP4922-EP; DIP-14_W7.62mm

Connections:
3V3: J4.5, J5.3, R17.1, RV1.1, U2.1 (VDD), U2.9 (~SHDN), U2.11 (VrefB), U2.13 (VrefA)
A0: J2#2.1, R19.1
A1: J2#2.2, R20.1
A2: J2#2.3, R21.1
A3: J2#2.4, R22.1
GND: C1.2, C2.2, J1.2, J1.5, J2.2, J2.5, J4.6, J5.2, R18.2, R23.2, R24.2, R25.2, R26.2, RV1.3, U1.11 (V-), U2.8 (~LDAC), U2.12 (AVSS)
MOSI: J4.4, U2.5 (SDI)
unnamed: J1.1, R1.2
unnamed: J1.3, R2.2
unnamed: J1.4, R3.2
unnamed: J1.6, R4.2
unnamed: J2.1, R5.2
unnamed: J2.3, R6.2
unnamed: J2.4, R7.2
unnamed: J2.6, R8.2
unnamed: C2.1, J5.4, R28.1
unnamed: J5.5, R28.2, U2.10 (VoutB)
unnamed: C1.1, J5.6, R27.1
unnamed: J5.7, R27.2, U2.14 (VoutA)
unnamed: R10.1, R20.2, R25.1, U1.7
unnamed: R11.1, R21.2, R24.1, U1.8
unnamed: R12.1, R22.2, R23.1, U1.14
unnamed: R13.1, R14.1, R15.1, R16.1, R17.2, R18.1, RV1.2
unnamed: R9.1, R19.2, R26.1, U1.1
unnamed: R1.1, R13.2, U1.3 (+)
unnamed: R2.1, R9.2, U1.2 (-)
unnamed: R3.1, R14.2, U1.5 (+)
unnamed: R4.1, R10.2, U1.6 (-)
unnamed: R5.1, R15.2, U1.10 (+)
unnamed: R6.1, R11.2, U1.9 (-)
unnamed: R7.1, R16.2, U1.12 (+)
unnamed: R8.1, R12.2, U1.13 (-)
RX: J4.1, U2.3 (~CS)
SCK: J4.2, U2.4 (SCK)
VBUS: J4.7, J5.1, U1.4 (V+)

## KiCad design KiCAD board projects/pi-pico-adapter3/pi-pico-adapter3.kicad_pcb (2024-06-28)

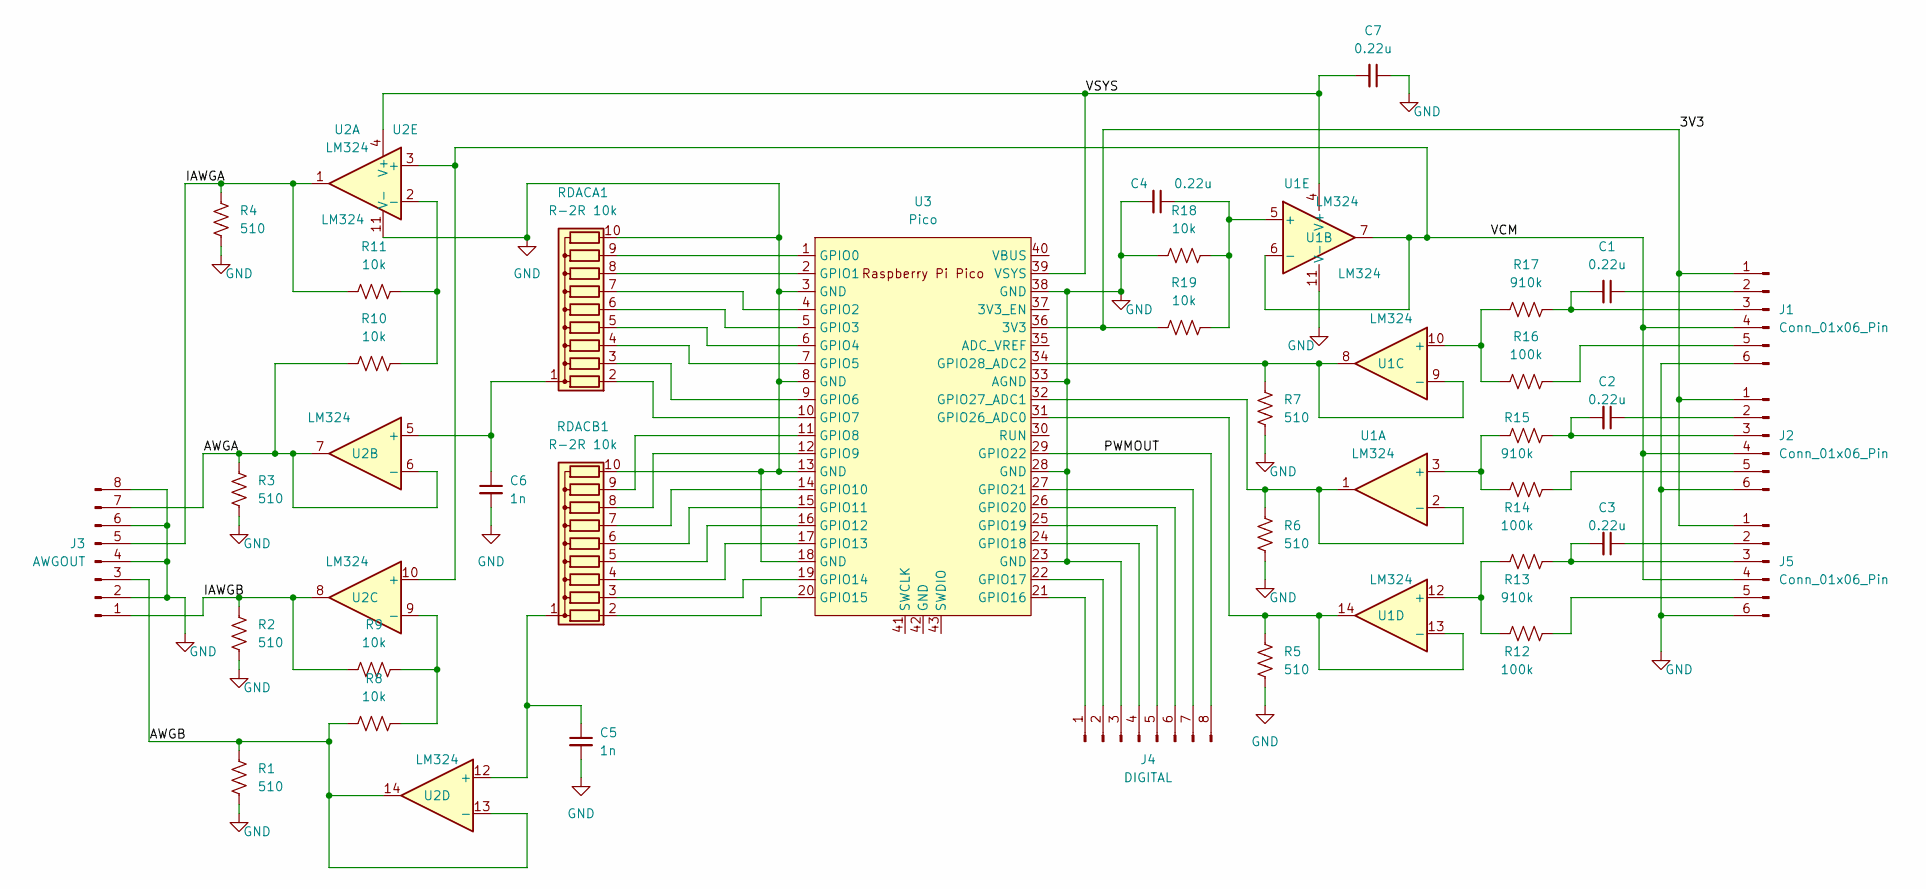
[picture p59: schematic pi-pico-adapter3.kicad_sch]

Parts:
C1, C2, C3, C4, C7: 0.22u; C_Rect_L7.0mm_W3.5mm_P2.50mm_P5.00mm
C5, C6: 1n; C_Rect_L7.0mm_W3.5mm_P2.50mm_P5.00mm
J1, J2, J5: Conn_01x06_Pin; PinHeader_1x06_P2.54mm_Vertical
J3: AWGOUT; PinHeader_1x08_P2.54mm_Vertical
J4: DIGITAL; PinHeader_1x08_P2.54mm_Vertical
R1, R2, R3, R4, R5, R6, R7: 510; R_Axial_DIN0204_L3.6mm_D1.6mm_P7.62mm_Horizontal
R8, R9, R10, R11, R18, R19: 10k; R_Axial_DIN0204_L3.6mm_D1.6mm_P7.62mm_Horizontal
R12, R14, R16: 100k; R_Axial_DIN0204_L3.6mm_D1.6mm_P7.62mm_Horizontal
R13, R15, R17: 910k; R_Axial_DIN0204_L3.6mm_D1.6mm_P7.62mm_Horizontal
RDACA1: R-2R 10k; R_Array_SIP10
RDACB1: R-2R 10k; R_Array_SIP10
U1, U2: LM324; DIP-14_W7.62mm
U3: Pico; RPi_Pico_SMD_TH

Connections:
/3V3: J1.1, J2.1, J5.1, R19.1, U3.36 (3V3)
/AWGA: J3.7, R3.1, R10.1, U2.6 (-), U2.7
/AWGB: J3.3, R1.1, R8.1, U2.13 (-), U2.14
/IAWGA: J3.5, R4.1, R11.1, U2.1
/IAWGB: J3.1, R2.1, R9.1, U2.8
/PWMOUT: J4.8, U3.29 (GPIO22)
/VCM: J1.4, J2.4, J5.4, U1.6 (-), U1.7, U2.3 (+), U2.10 (+)
/VSYS: C7.2, U1.4 (V+), U2.4 (V+), U3.39 (VSYS)
GND: C4.2, C5.2, C6.2, C7.1, J1.6, J2.6, J3.2, J3.4, J3.6, J3.8, J4.3, J5.6, R1.2, R2.2, R3.2, R4.2, R5.2, R6.2, R7.2, R18.1, RDACA1.10 (R9), RDACB1.10 (R9), U1.11 (V-), U2.11 (V-), U3.3 (GND), U3.8 (GND), U3.13 (GND), U3.18 (GND), U3.23 (GND), U3.28 (GND), U3.33 (AGND), U3.38 (GND)
unnamed: C1.1, J1.2
unnamed: C1.2, J1.3, R17.2
unnamed: J1.5, R16.2
unnamed: C2.1, J2.2
unnamed: C2.2, J2.3, R15.2
unnamed: J2.5, R14.2
unnamed: J4.1, U3.21 (GPIO16)
unnamed: J4.2, U3.22 (GPIO17)
unnamed: J4.4, U3.24 (GPIO18)
unnamed: J4.5, U3.25 (GPIO19)
unnamed: J4.6, U3.26 (GPIO20)
unnamed: J4.7, U3.27 (GPIO21)
unnamed: C3.1, J5.2
unnamed: C3.2, J5.3, R13.2
unnamed: J5.5, R12.2
unnamed: RDACA1.2 (R1), U3.10 (GPIO7)
unnamed: RDACA1.3 (R2), U3.9 (GPIO6)
unnamed: RDACA1.4 (R3), U3.7 (GPIO5)
unnamed: RDACA1.5 (R4), U3.6 (GPIO4)
unnamed: RDACA1.6 (R5), U3.5 (GPIO3)
unnamed: RDACA1.7 (R6), U3.4 (GPIO2)
unnamed: RDACA1.8 (R7), U3.2 (GPIO1)
unnamed: RDACA1.9 (R8), U3.1 (GPIO0)
unnamed: C6.1, RDACA1.1 (common), U2.5 (+)
unnamed: RDACB1.2 (R1), U3.20 (GPIO15)
unnamed: RDACB1.3 (R2), U3.19 (GPIO14)
unnamed: RDACB1.4 (R3), U3.17 (GPIO13)
unnamed: RDACB1.5 (R4), U3.16 (GPIO12)
unnamed: RDACB1.6 (R5), U3.15 (GPIO11)
unnamed: RDACB1.7 (R6), U3.14 (GPIO10)
unnamed: RDACB1.8 (R7), U3.12 (GPIO9)
unnamed: RDACB1.9 (R8), U3.11 (GPIO8)
unnamed: C5.1, RDACB1.1 (common), U2.12 (+)
unnamed: R14.1, R15.1, U1.3 (+)
unnamed: R6.1, U1.1, U1.2 (-), U3.32 (GPIO27_ADC1)
unnamed: C4.1, R18.2, R19.2, U1.5 (+)
unnamed: R16.1, R17.1, U1.10 (+)
unnamed: R7.1, U1.8, U1.9 (-), U3.34 (GPIO28_ADC2)
unnamed: R12.1, R13.1, U1.12 (+)
unnamed: R5.1, U1.13 (-), U1.14, U3.31 (GPIO26_ADC0)
unnamed: R10.2, R11.2, U2.2 (-)
unnamed: R8.2, R9.2, U2.9 (-)

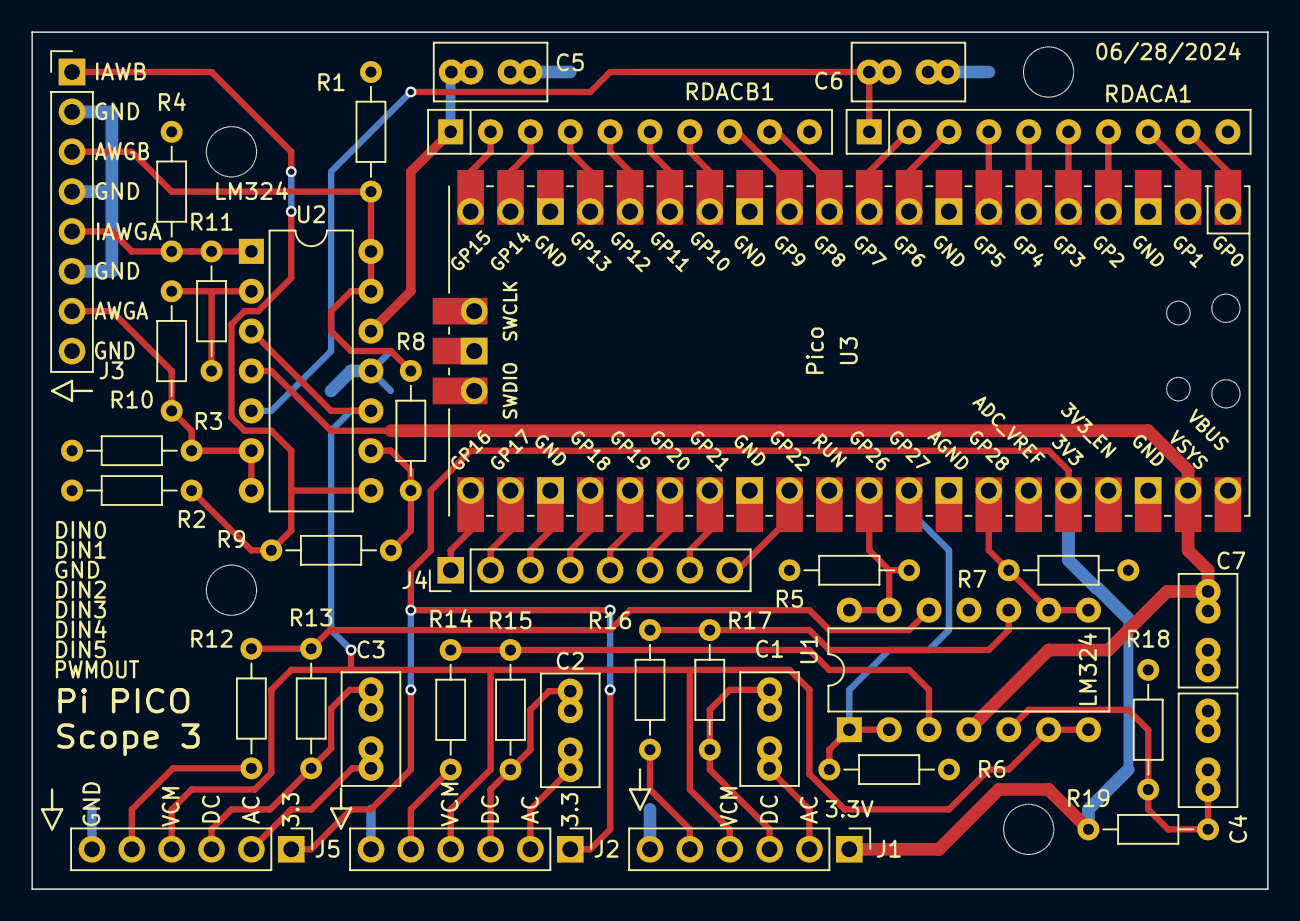
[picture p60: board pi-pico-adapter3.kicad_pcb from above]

Board: 2 copper layers, 78.7 x 54.6 mm, 40 parts (0 on the bottom side), 51 nets.

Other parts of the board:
MH1, MH2, MH3, MH4: MountingHole_3.2mm

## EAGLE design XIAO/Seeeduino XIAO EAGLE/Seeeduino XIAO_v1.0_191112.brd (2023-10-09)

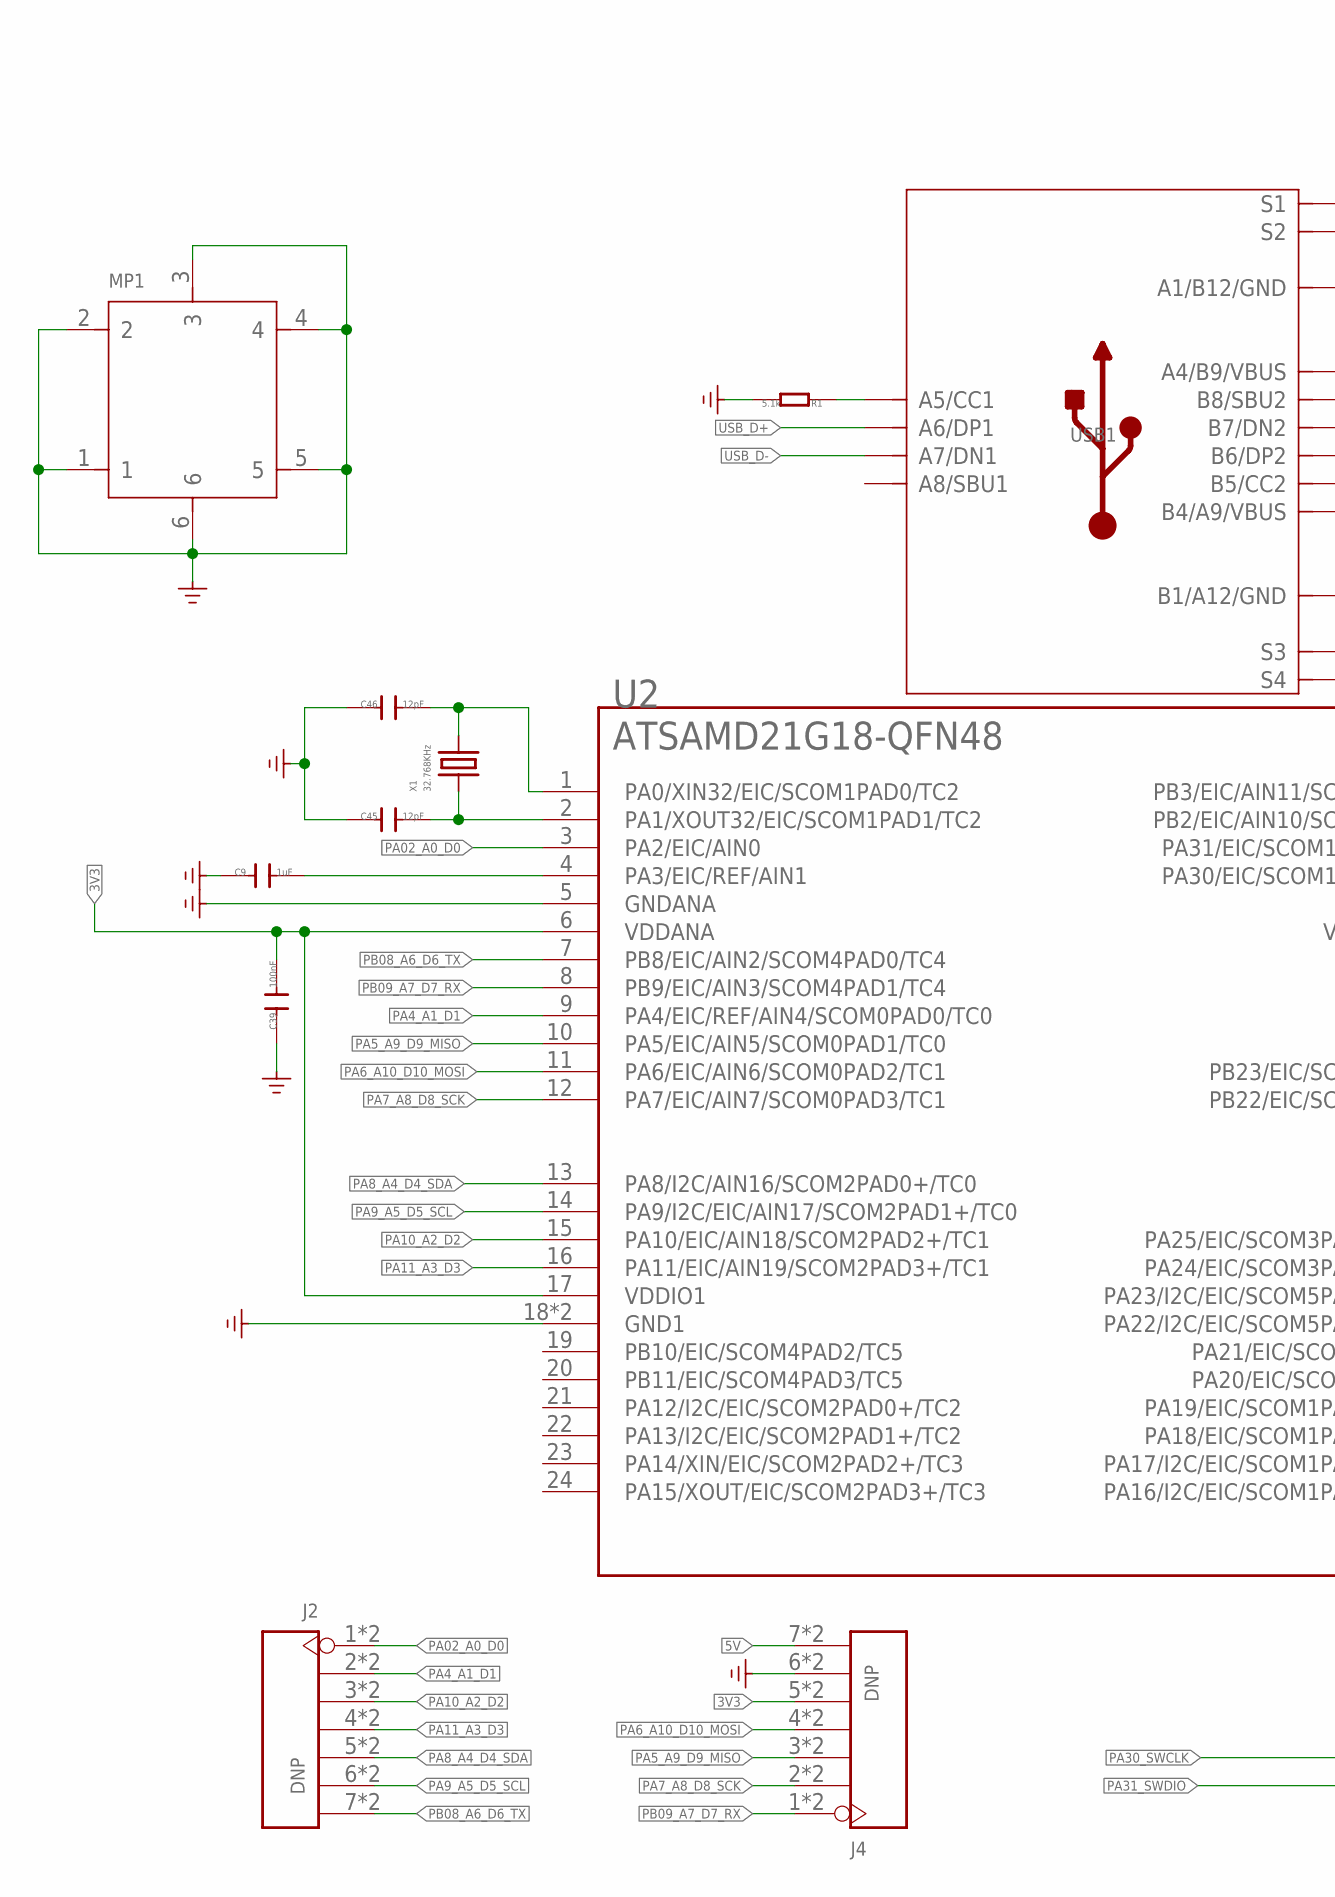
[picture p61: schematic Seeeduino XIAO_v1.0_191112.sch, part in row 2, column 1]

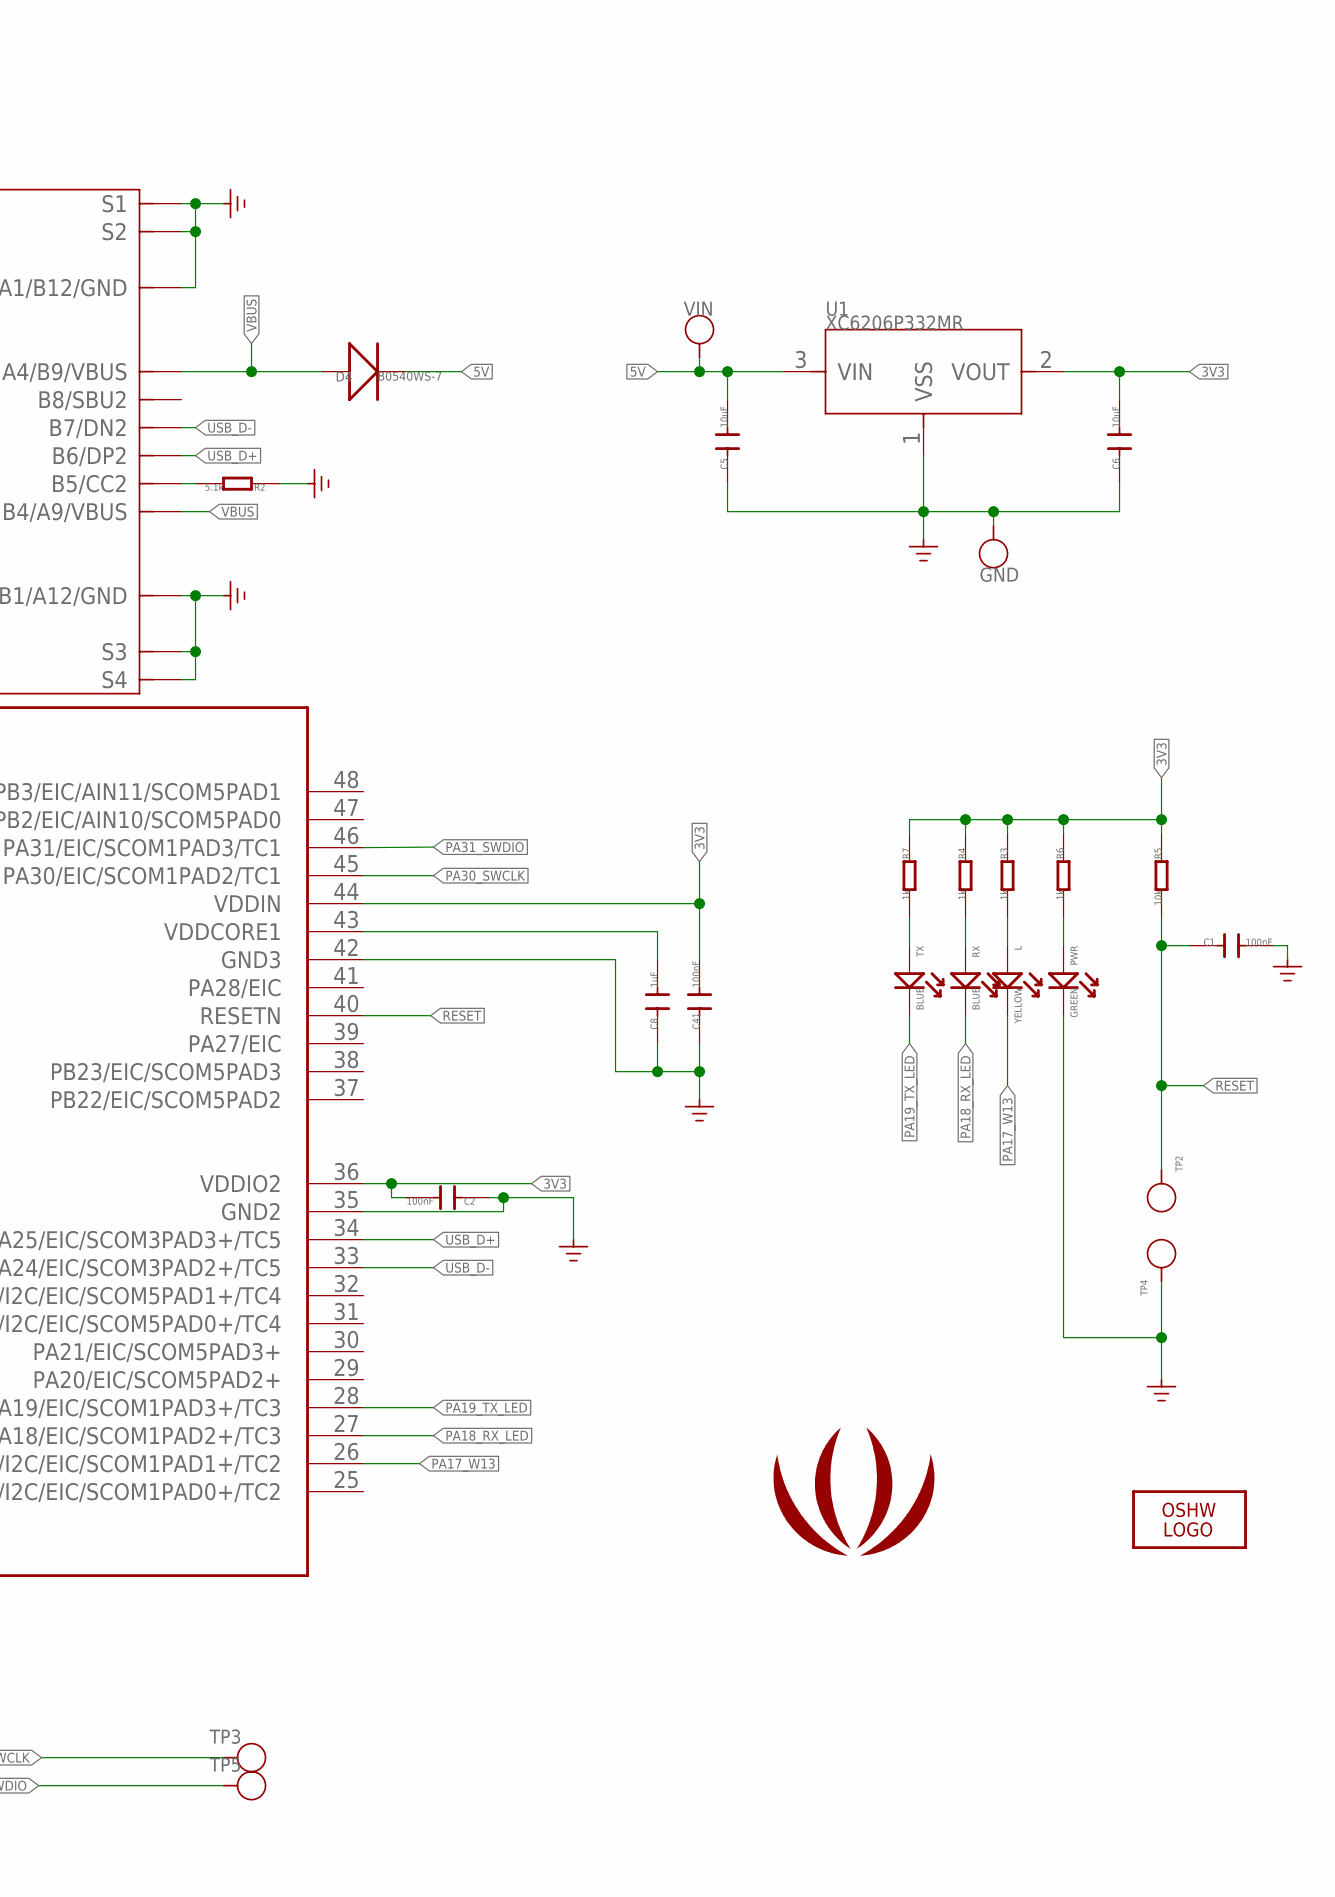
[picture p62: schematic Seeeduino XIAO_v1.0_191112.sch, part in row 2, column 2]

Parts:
C1, C2, C39, C41: 100nF; C0402
C5, C6: 10uF; C0603
C8, C9: 1uF; C0402
C45, C46: 12pF; C0402
D4: B0540WS-7; SOD323
GND: TEST-POINT'4080'; TP-80X40MIL
J2, J4: DNP; H7-HALF-HOLE-2.54
L: YELLOW; LED-0402
LOGO1: LOGO-OSHW-FILLX0200-NT; OSHW_FILLX200_NOTEXT
MP1: SHIELDING-COVER-12.3X11.9X0.2MM
PWR: GREEN; LED-0402
R1, R2: 5.1k; R0402
R3, R4, R6, R7: 1k; R0402
R5: 10k; R0402
RX: BLUE; LED-0402
TP2, TP3, TP4, TP5: TEST-POINT'4545'; TP-D45MIL
TX: BLUE; LED-0402
U1: XC6206P332MR; SOT-23
U2: ATSAMD21G18-QFN48; QFN48-7X7
U$3: LOGO-SEEED-BIG-SILK; SEEED-SILK-280*268MIL
USB1: USB2.0-TYPE-C
VIN: TEST-POINT'4080'; TP-80X40MIL
X1: 32.768KHz; X2-SMD-L2.0X1.2X0.55MM

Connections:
3V3: C2.2, C6.2, C39.2, C41.2, J4.5, J4.17 (5), R3.1, R4.1, R5.1, R6.1, R7.1, U1.2 (VOUT), U2.6 (VDDANA), U2.17 (VDDIO1), U2.36 (VDDIO2), U2.44 (VDDIN)
5V: C5.2, D4.-, J4.7, J4.19 (7), U1.3 (VIN), VIN.1
GND: C1.2, C2.1, C5.1, C6.1, C8.1, C9.1, C39.1, C41.1, C45.1, C46.1, GND.1, J4.6, J4.18 (6), MP1.1, MP1.2, MP1.3, MP1.4, MP1.5, MP1.6, PWR.-, R1.2, R2.1, TP4.T, U1.1 (VSS), U2.5 (GNDANA), U2.18 (GND1), U2.35 (GND2), U2.42 (GND3), U2.PAD (GND1), USB1.A1_B12 (A1/B12/GND), USB1.B1_A12 (B1/A12/GND), USB1.S1, USB1.S2, USB1.S3, USB1.S4, USB1.S5 (S1), USB1.S6 (S2)
unnamed: R1.1, USB1.A5 (A5/CC1)
unnamed: R2.2, USB1.B5 (B5/CC2)
unnamed: C8.2, U2.43 (VDDCORE1)
unnamed: C9.2, U2.4 (PA3/EIC/REF/AIN1)
unnamed: L.+, R3.2
unnamed: R7.2, TX.+
unnamed: C45.2, U2.2 (PA1/XOUT32/EIC/SCOM1PAD1/TC2), X1.2
unnamed: R4.2, RX.+
unnamed: C46.2, U2.1 (PA0/XIN32/EIC/SCOM1PAD0/TC2), X1.1
unnamed: PWR.+, R6.2
PA02_A0_D0: J2.1, J2.13 (1), U2.3 (PA2/EIC/AIN0)
PA4_A1_D1: J2.2, J2.14 (2), U2.9 (PA4/EIC/REF/AIN4/SCOM0PAD0/TC0)
PA5_A9_D9_MISO: J4.3, J4.15 (3), U2.10 (PA5/EIC/AIN5/SCOM0PAD1/TC0)
PA6_A10_D10_MOSI: J4.4, J4.16 (4), U2.11 (PA6/EIC/AIN6/SCOM0PAD2/TC1)
PA7_A8_D8_SCK: J4.2, J4.14 (2), U2.12 (PA7/EIC/AIN7/SCOM0PAD3/TC1)
PA8_A4_D4_SDA: J2.5, J2.17 (5), U2.13 (PA8/I2C/AIN16/SCOM2PAD0+/TC0)
PA9_A5_D5_SCL: J2.6, J2.18 (6), U2.14 (PA9/I2C/EIC/AIN17/SCOM2PAD1+/TC0)
PA10_A2_D2: J2.3, J2.15 (3), U2.15 (PA10/EIC/AIN18/SCOM2PAD2+/TC1)
PA11_A3_D3: J2.4, J2.16 (4), U2.16 (PA11/EIC/AIN19/SCOM2PAD3+/TC1)
PA17_W13: L.-, U2.26 (PA17/I2C/EIC/SCOM1PAD1+/TC2)
PA18_RX_LED: RX.-, U2.27 (PA18/EIC/SCOM1PAD2+/TC3)
PA19_TX_LED: TX.-, U2.28 (PA19/EIC/SCOM1PAD3+/TC3)
PA30_SWCLK: TP3.T, U2.45 (PA30/EIC/SCOM1PAD2/TC1)
PA31_SWDIO: TP5.T, U2.46 (PA31/EIC/SCOM1PAD3/TC1)
PB08_A6_D6_TX: J2.7, J2.19 (7), U2.7 (PB8/EIC/AIN2/SCOM4PAD0/TC4)
PB09_A7_D7_RX: J4.1, J4.13 (1), U2.8 (PB9/EIC/AIN3/SCOM4PAD1/TC4)
RESET: C1.1, R5.2, TP2.T, U2.40 (RESETN)
USB_D+: U2.34 (PA25/EIC/SCOM3PAD3+/TC5), USB1.A6 (A6/DP1), USB1.B6 (B6/DP2)
USB_D-: U2.33 (PA24/EIC/SCOM3PAD2+/TC5), USB1.A7 (A7/DN1), USB1.B7 (B7/DN2)
VBUS: D4.+, USB1.A4_B9 (A4/B9/VBUS), USB1.B4_A9 (B4/A9/VBUS)

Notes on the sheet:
2019.11.12
Jienian.Feng
v1.0
Initail Version

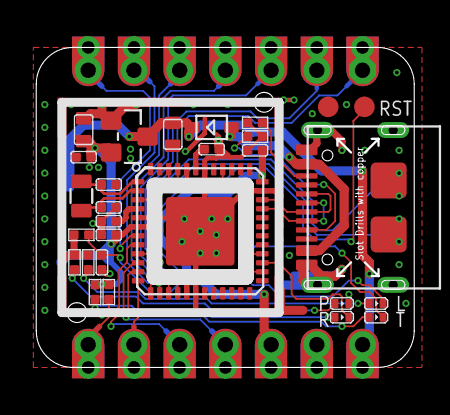
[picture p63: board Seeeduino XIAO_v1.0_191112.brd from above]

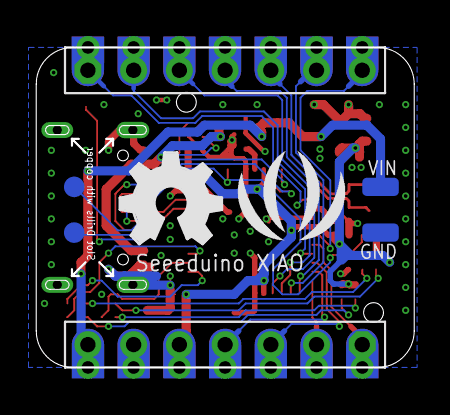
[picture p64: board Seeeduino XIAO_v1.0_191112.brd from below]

Board: 2 copper layers, 21.0 x 17.8 mm, 37 parts (6 on the bottom side), 33 nets.

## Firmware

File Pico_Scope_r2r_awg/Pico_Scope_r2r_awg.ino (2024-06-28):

//Pico_Scope3 3 channel scope with dual 8 bit R2R ladder DAC AWG
// 6/01/2024
#include "pico/stdlib.h"
#include "hardware/adc.h"
#include "hardware/pwm.h"
#include <hardware/timer.h>
#include <hardware/irq.h>
#include "pico/multicore.h"

#define ALARM_NUM 1
#define ALARM_IRQ TIMER_IRQ_1

uint8_t scopea[16384]; // 14336/8 ~ 1700 max samples
//  uint8_t digin[4096];
uint8_t awgouta[4096];
uint8_t awgoutb[4096];

short led = 25;
short awgon;
//short awgonb;
short addr;
short data;
short awgdata;
short awgres;
short n;
short m;
uint32_t tg;
short sync = 0;
short point = 0;
float Step;
unsigned int at, at2, st, st2, stReal;
short bmax=4096;
short amax=4096;
short bs=1024;
uint16_t tbs=2048;
uint16_t rbs=3072;
uint16_t fbs=4096;
uint16_t vbs=5120;
uint16_t sbs=6144;
uint16_t ebs=7168;
uint16_t gbs=8192;
short dy=1;
uint16_t ns=1024;
uint16_t ms=1024;
int pwmf = 500;
int pwid = 500;

static void alarm_irq(void) {
  hw_clear_bits(&timer_hw->intr, 1u << ALARM_NUM);
  alarm_in_us_arm(at);
  if (awgon == 1){
    if (n >= ns) n = 0;
    if (m >= ms) m = 0;
    awgdata = (awgoutb[m] << 8) + awgouta[n];
    gpio_put_masked(0x0FFFF, awgdata);
    n++;
    m++;
  }
  else {
    n = 0;
    m = 0;
  }
}

static void alarm_in_us_arm(uint32_t delay_us) {
  uint64_t target = timer_hw->timerawl + delay_us;
  timer_hw->alarm[ALARM_NUM] = (uint32_t) target;
}

static void alarm_in_us(uint32_t delay_us) {
  hw_set_bits(&timer_hw->inte, 1u << ALARM_NUM);
  irq_set_exclusive_handler(ALARM_IRQ, alarm_irq);
  irq_set_enabled(ALARM_IRQ, true);
  alarm_in_us_arm(at);
}

void setup1() {
  at=20;
  awgon = 0; // default AWG off
  alarm_in_us(at);
}

void loop1() {
  
}
  
void setup() {
  
  Serial.begin(2000000);
  pinMode(led, OUTPUT);
  pinMode(0, OUTPUT);
  pinMode(1, OUTPUT);
  pinMode(2, OUTPUT);
  pinMode(3, OUTPUT);
  pinMode(4, OUTPUT);
  pinMode(5, OUTPUT);
  pinMode(6, OUTPUT);
  pinMode(7, OUTPUT);
  pinMode(8, OUTPUT);
  pinMode(9, OUTPUT);
  pinMode(10, OUTPUT);
  pinMode(11, OUTPUT);
  pinMode(12, OUTPUT);
  pinMode(13, OUTPUT);
  pinMode(14, OUTPUT);
  pinMode(15, OUTPUT);
  pinMode(16, INPUT);
  pinMode(17, INPUT);
  pinMode(18, INPUT);
  pinMode(19, INPUT);
  pinMode(20, INPUT);
  pinMode(21, INPUT);
  analogWriteFreq(pwmf);
  analogWriteRange(1000);
  adc_init();
  adc_gpio_init(26); // ADC0
  adc_gpio_init(27); // ADC1
  adc_gpio_init(28); // ADC2
  adc_gpio_init(29); // ADC3
  adc_select_input(0); 
  //alarm_in_us(at);
} 

void loop() {
  
  int measa;
  int measb;
  int measc;
  int digmeas;
  int VDD;
  char c, c2;
  uint32_t ta, TotalReal, StartReal;
  st=11;
  awgres = 255;
  at=20;
  short Ain1;
  Ain1 = 0; // 26; // pin number for A1
  short Ain2;
  Ain2 = 1; // 27; // pin number for A2
  short Ain3;
  Ain3 = 2; // 28; // pin number for A3
  short Ain4;
  Ain4 = 3; // 29; // pin number for A4

  while (true) { 
    if (Serial.available()){
      c=Serial.read();
      switch (c){
        case 'I': // read back FW Rev
          Serial.println ("Pi Pico Scope R2R 3.0");
          break;
        case 'T': // change the AWG value of at in uSec both channels must be same rate
          at2 = Serial.parseInt();
          if(at2>0){
            at=at2;
          }
          break;
        case 'N': // change number of AWG A samples 
          ns = Serial.parseInt();
          if(ns>bmax){
            ns=bmax;
          }
          break;
        case 'M': // change number of AWG B samples 
          ms = Serial.parseInt();
          if(ms>bmax){
            ms=bmax;
          }
          break;
        case 'L': // load AWG A Buffer data
          addr = Serial.parseInt();
          if(addr > 2047){
              addr=2047;
            }
            if(addr < 0){
              addr=0;
            }
          c2 = Serial.read();
          if(c2=='D'){
            data = Serial.parseInt();
            if(data > awgres){
              data=awgres;
            }
            if(data < 0){
              data=0;
            }
          } else {
            data = 0;
          }
          awgouta[addr] = data; // | 0b0111000000000000; // address DACA
          break;
        case 'l': // load AWG B Buffer data
          addr = Serial.parseInt();
          if(addr > 2047){
              addr=2047;
            }
            if(addr < 0){
              addr=0;
            }
          c2 = Serial.read();
          if(c2=='D'){
            data = Serial.parseInt();
            if(data > awgres){
              data=awgres;
            }
            if(data < 0){
              data=0;
            }
          } else {
            data = 0;
          }
          awgoutb[addr] = data; //| 0b1111 0000 0000 0000; // address DACB
          break;
        case 't': // change the Scope value of dt in uSec
          st2 = Serial.parseInt();
          if(st2>0){
            st=st2;
          }
          break;
        case 'b': // change number of samples to capture
          bs = Serial.parseInt();
          if(bs>bmax){
            bs=bmax;
          }
          tbs = bs * 2;
          rbs = bs * 3;
          fbs = bs * 4;
          vbs = bs * 5;
          sbs = bs * 6;
          ebs = bs * 7;
          gbs = bs * 8;
          break;
        case 'G': // enable - disable AWG A output
          c2 = Serial.read();
          if(c2=='o'){
            awgon = 1;
          }else{
            awgon = 0;
          }
          break;
        case 'g': // enable - disable AWG A output
          c2 = Serial.read();
          if(c2=='o'){
            awgon = 1;
          }else{
            awgon = 0;
          }
          break;
        case 'R': // Reset AWG start point at start of aquire
          sync = Serial.parseInt();
          break;
        case 'r': // Set AWG start address when case R > 0
          point = Serial.parseInt();
          break;
        case 's': // enable - disable PWM output
          c2 = Serial.read();
          if(c2=='o'){
            analogWrite (22, pwid); 
          }else{
            analogWrite (22, 0); 
          }
          break;
        case 'p': // change analog write pwm frequency value
          pwmf = Serial.parseInt();
          analogWriteFreq( pwmf );
          break;
        case 'm': // change pwm duty cycle % 
          pwid = Serial.parseInt(); // range from 0 (0%) to 1000 (100%)
          break;
        case 'V': // Read back the 3.3 V supply voltage divider 1/3
          adc_select_input(3);
          sleep_ms(1);
          VDD=adc_read();
          Serial.print ("V=");
          Serial.println ((int) VDD);
          break;
        case 'A': // set input pin value for scope channel Ain1
          Ain1 = Serial.parseInt();
          break;
        case 'B': // set input pin value for scope channel Ain2
          Ain2 = Serial.parseInt();
          break;
        case 'C': // set input pin value for scope channel Ain3
          Ain3 = Serial.parseInt();
          break;
        case 'D': // set input pin value for scope channel Ain4
          Ain4 = Serial.parseInt();
          break;
        case '1': // do scope ch a single capture
        // if sync is on reset start of awg buffer pointer
          if (sync > 0 ) {
            if (awgon == 1){
              awgon = 0;
              while ( n != point) {
               n = point;
                m = point;
              }
              delayMicroseconds(6);
              awgon = 1;
              delayMicroseconds(sync);
            }
          }
          ta = time_us_32();
          adc_select_input(Ain1);
          StartReal = ta;
          for (int i = 0; i < bs; i++){ // Fill Buffer
            measa = adc_read(); // analogRead(A1);
            scopea[i] = (measa & 0xFF00) >> 8;
            scopea[i+bs] = measa & 0xFF;
            ta+=st;
            while (ta>time_us_32());
          }
          TotalReal=time_us_32()-StartReal;
          //stReal=TotalReal/bs; // calculate the average time for each reading
          digitalWrite(led, HIGH); // Toggel LED High while sending data
          Serial.print("stReal= ");
          Serial.println(TotalReal); // report total time for bs samples
          // dump buffer over serial
          Serial.write(scopea, tbs);
          Serial.println("");
          //
          digitalWrite(led, LOW);
          break;
          //
        case '2': // do scope ch a and b single capture
        // if sync is on reset start of awg buffer pointer
          if (sync > 0 ) {
            if (awgon == 1){
              awgon = 0;
              while ( n != point) {
               n = point;
                m = point;
              }
              delayMicroseconds(6);
              awgon = 1;
              delayMicroseconds(sync);
            }
          }
          ta = time_us_32();
          StartReal = ta;
          for (int i = 0; i < bs; i++){ // Fill Buffer
            adc_select_input(Ain1);
            measa = adc_read();
            adc_select_input(Ain2);
            measb = adc_read();
            scopea[i] = (measa & 0xFF00) >> 8;
            scopea[i+bs] = measa & 0xFF;
            scopea[i+tbs] = (measb & 0xFF00) >> 8;
            scopea[i+rbs] = measb & 0xFF;
            ta+=st;
            while (ta>time_us_32());
          }
          TotalReal=time_us_32()-StartReal;
          //stReal=TotalReal/bs; // calculate the average time for each reading
          digitalWrite(led, HIGH); // Toggel LED High while sending data
          Serial.print("stReal= ");
          Serial.println(TotalReal);
          // Dump Buffer over serial
          Serial.write(scopea, fbs);
          Serial.println("");
          //
          digitalWrite(led, LOW);  // turn the LED off (HIGH is the voltage level)
          break;
          //
        case '3': // do scope ch a b and c single capture
        // if sync is on reset start of awg buffer pointer
          if (sync > 0 ) {
            if (awgon == 1){
              awgon = 0;
              while ( n != point) {
               n = point;
                m = point;
              }
              delayMicroseconds(6);
              awgon = 1;
              delayMicroseconds(sync);
            }
          }
          ta = time_us_32();
          StartReal = ta;
          for (int i = 0; i < bs; i++){ // Fill Buffer
            adc_select_input(Ain1);
            measa = adc_read();
            adc_select_input(Ain2);
            measb = adc_read();
            adc_select_input(Ain3);
            measc = adc_read();
            scopea[i] = (measa & 0xFF00) >> 8;
            scopea[i+bs] = measa & 0xFF;
            scopea[i+tbs] = (measb & 0xFF00) >> 8;
            scopea[i+rbs] = measb & 0xFF;
            scopea[i+fbs] = (measc & 0xFF00) >> 8;
            scopea[i+vbs] = measc & 0xFF;
            ta+=st;
            while (ta>time_us_32());
          }
          TotalReal=time_us_32()-StartReal;
          //stReal=TotalReal/bs; // calculate the average time for each reading
          digitalWrite(led, HIGH); // Toggel LED High while sending data
          Serial.print("stReal= ");
          Serial.println(TotalReal);
          // Dump Buffer over serial
          Serial.write(scopea, sbs);
          Serial.println("");
          //
          digitalWrite(led, LOW);  // turn the LED off (HIGH is the voltage level)
          break;
      }
    }
  }
}

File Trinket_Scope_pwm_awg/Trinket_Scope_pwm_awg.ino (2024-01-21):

//Trinket M0 Scope3 1/2/3 channel scope 1 internal awg (1/18/2024)
//
//#include "arduino_m0_tweak.hpp"
#include <Adafruit_ZeroTimer.h>

#ifndef MULTIPLE_PIN_OPS_H
#define MULTIPLE_PIN_OPS_H
//

void multiplePinMode(const int *pins, const int numberOfPins, uint8_t mode);
void multipleDigitalWrite(const int *pins, const int numberOfPins, uint16_t number);
uint64_t multipleDigitalRead(const int *pins, const int numberOfPins);
void multipleAnalogRead(const int *pins, const int numberOfPins, int *values);
void multipleAnalogWrite(const int *pins, const int numberOfPins, uint8_t* values);

#endif // MULTIPLE_PIN_OPS_H
// timer tester
Adafruit_ZeroTimer zerotimer = Adafruit_ZeroTimer(3);

uint8_t scopea[4096];
uint8_t scopeb[4096];
uint8_t scopec[4096]; 
uint8_t digin[2048];
short awgouta[2048];
short awgoutb[2048];
int wavea;
int cyclea;
int ampla;
int offseta;
int awgon;
int awgpwnon;
int addr;
int data;
int awgdata;
int n;
int m;
int sync = 0;
float Step;
unsigned int at, at2, st, st2, stReal;
int bmax=2048;
int bs=1024;
int tbs=2048;
int ns=1024;
int ms=1024;
int pwmf = 500;
int pwid = 500;
//
void TC3_Handler() {
  Adafruit_ZeroTimer::timerHandler(3);
}
//
static inline void syncADC() {
  // Taken from `hri_adc_d21.h`
  while (ADC->STATUS.bit.SYNCBUSY == 1) {}
}
void ADC_init() {
  /* Increase the ADC clock by setting the PRESCALER from default DIV128 to a
  smaller divisor. This is needed for DAQ rates larger than ~20 kHz on SAMD51
  and DAQ rates larger than ~10 kHz on SAMD21. Setting too small divisors will
  result in ADC errors. Keep as large as possible to increase ADC accuracy.

  SAMD21:
    ADC input clock is default at 48 MHz (Generic Clock Generator 0).
    \.platformio\packages\framework-arduino-samd\cores\arduino\wiring.c

    Max ADC input clock frequency    :  48 MHz    (datasheet table 37-7)
    Max ADC internal clock frequency : 2.1 MHz    (datasheet table 37-24)

    Handy calculator:
    https://blog.thea.codes/getting-the-most-out-of-the-samd21-adc/

  */

  // Turn off ADC
  ADC->CTRLA.reg = 0;
  syncADC();

  // Load the factory calibration
  uint32_t bias =
      (*((uint32_t *)ADC_FUSES_BIASCAL_ADDR) & ADC_FUSES_BIASCAL_Msk) >>
      ADC_FUSES_BIASCAL_Pos;
  uint32_t linearity =
      (*((uint32_t *)ADC_FUSES_LINEARITY_0_ADDR) & ADC_FUSES_LINEARITY_0_Msk) >>
      ADC_FUSES_LINEARITY_0_Pos;
  linearity |= ((*((uint32_t *)ADC_FUSES_LINEARITY_1_ADDR) &
                 ADC_FUSES_LINEARITY_1_Msk) >>
                ADC_FUSES_LINEARITY_1_Pos)
               << 5;

  ADC->CALIB.reg =
      ADC_CALIB_BIAS_CAL(bias) | ADC_CALIB_LINEARITY_CAL(linearity);
  // No sync needed according to `hri_adc_d21.h`

  // The ADC clock must remain below 2.1 MHz, see SAMD21 datasheet table 37-24.
  // Hence, don't go below DIV32 @ 48 MHz.
  ADC->CTRLB.bit.PRESCALER = ADC_CTRLB_PRESCALER_DIV16_Val;
  syncADC();

  // AnalogRead resolution
  ADC->CTRLB.bit.RESSEL = ADC_CTRLB_RESSEL_16BIT_Val;
  syncADC();

  // Sample averaging
  ADC->AVGCTRL.bit.SAMPLENUM = ADC_AVGCTRL_SAMPLENUM_1_Val;
  // No sync needed according to `hri_adc_d21.h`
  ADC->AVGCTRL.bit.ADJRES = 1; // 2^N, must match `ADC0->AVGCTRL.bit.SAMPLENUM`
  // No sync needed according to `hri_adc_d21.h`

  // Sampling length, larger means increased max input impedance
  // default 63, stable 32 @ DIV32 & SAMPLENUM_4
  ADC->SAMPCTRL.bit.SAMPLEN = 2;
  // No sync needed according to `hri_adc_d21.h`

  ADC->CTRLB.bit.DIFFMODE = 0;
  syncADC();
  ADC->INPUTCTRL.bit.MUXPOS = g_APinDescription[A1].ulADCChannelNumber;
  syncADC();
  ADC->INPUTCTRL.bit.MUXNEG = ADC_INPUTCTRL_MUXNEG_GND_Val;
  syncADC();
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

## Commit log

2023-10-09 First upload of source files for XIAO scope
    First up load of all the source material for the XIAO arduino scope interface for use with Universal ALICE.
    [Seeeduino XIAO_v1.0_191112.brd, Seeeduino XIAO_v1.0_191112.sch, XIAO-scope-Sketch.fzz, XIAO-scope-awg-pwm.fzz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]
2023-10-31 Add Arduino How to install
    Adding files on how to set up Arduino for compiling XIAO SAMD21 code.
2023-11-03 Firmware upload
    Added up loadable precompiled firmware file and steps to put board in to bootloader.
2023-12-22 Weekly Update 12/22/2023
    Weekly update for 12/22/2023.
    New faster sample rates for SAMD21 based boards.
2023-12-29 Weekly Update 29 Dec 2023
    Weekly update for Dec 29 2023. New source and .uf2 files for SAMD21 based boards. Add more hardware board options to Hardware list.
2024-01-04 Add Linux udev rules file
    Add Linux udev rules file to access USB boards
2024-01-13 Weekly Update for Jan 13 2024
    New faster PWM AWG output channels for SAMD21 based boards
    Add two SparkFun boards.
2024-03-16 Weekly Up Date to Arduino code for certain hardware.
    Weekly update to XIAO, Qt Py and M4 Express hardware to speed up 4 channel input support and to add AWG DAC output look back through analog input Mux.
2024-06-28 Post ASEE first up-date
    This will be the first of the post ASEE up-dates. Now including KiCAD project boards.
    [diff-probe-x4-v2-B_Cu.gbr, diff-probe-x4-v2-B_Mask.gbr, diff-probe-x4-v2-B_Silkscreen.gbr, diff-probe-x4-v2-Edge_Cuts.gbr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]
